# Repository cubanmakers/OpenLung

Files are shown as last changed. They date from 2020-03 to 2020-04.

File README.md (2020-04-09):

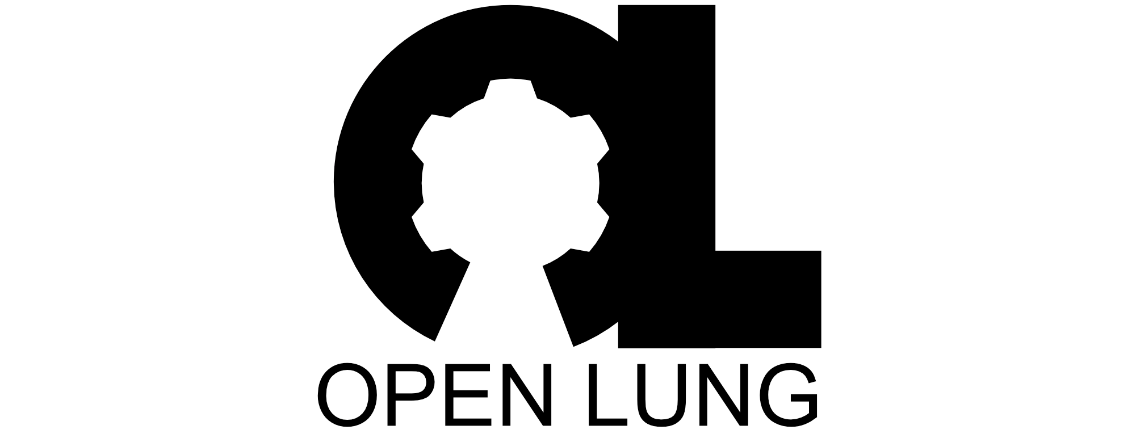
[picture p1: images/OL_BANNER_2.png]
OpenLung


# Disclaimer

*The plans, documents and other materials (“Material”) contained on this website are intended to facilitate the design of a prototype reproducible medical device to be used if required during the Covid-19 pandemic. The Material is not itself a medical device. The Material has not been tested and has not been approved for use in humans or animals by any regulatory authority of any country.*

*By using the Material, you are agreeing to the following disclaimer.*

*OpenLung / Open Source Ventilator offers the Material as-is and as-available, and makes no representations or warranties of any kind whatever concerning the Material, whether express, implied, statutory, or other. This includes, without limitation, warranties of merchantability, fitness for a particular purpose, non-infringement, absence of latent or other defects, accuracy, or the presence or absence of errors, whether or not known or discoverable.*

*To the extent possible, in no event will OpenLung / Open Source Ventilator be liable to you on any legal theory (including, without limitation, negligence) or otherwise for any direct, special, indirect, incidental, consequential, punitive, exemplary, or other losses, costs, expenses, or damages arising out of the Material or use of the Material, even if OpenLung / Open Source Ventilator has been advised of the possibility of such losses, costs, expenses, or damages.*

*Any ventilator system that has not been approved by a competent medical device regulatory authority may not deliver to the user the ability to properly monitor and control tidal volume, inspiratory pressure, inspiratory: expiratory ratio, heart rate, nor provide the user with the ability to monitor and control positive-end expiratory pressure (PEEP), peak inspiratory pressure (PIP) or to adapt to individual patient requirements.  Inability to monitor and/or control any of these factors can cause death or serious permanent injury.*

*The disclaimer of warranties and limitation of liability provided above shall be interpreted in a manner that, to the extent possible, most closely approximates an absolute disclaimer and waiver of all liability.*

# Low Resource Bag Valve Mask (BVM) Ventilator

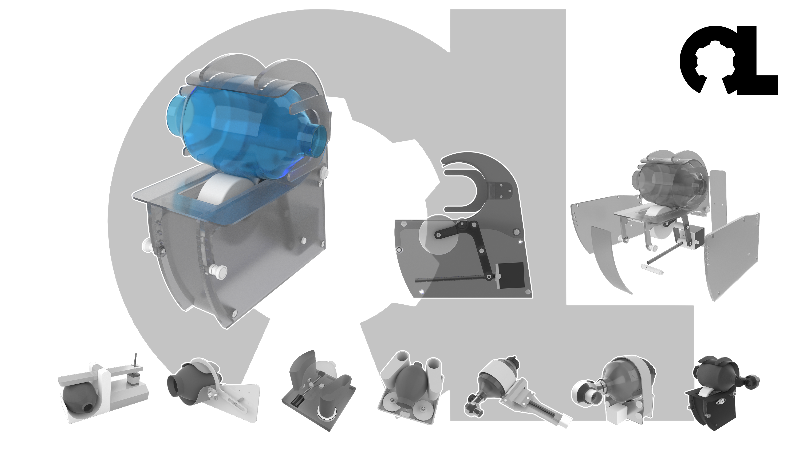
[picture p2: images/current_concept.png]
Current Mechanical Concept


- This project was jumpstarted by the COVID-19 global pandemic as a result of the community discussion on a Facebook group called Open Source COVID19 and OpenSourceVentilator, this is why I created a GitLab project for a new open-source product called **OpenLung**.
- More specifically, this project was created in a discussion surrounding low cost **Bag Valve Mask** (**BVM** or **AmbuBag**)-based emergency respirators wherein prior solutions had been developed.
- The first device discussed came from an [MIT research group](https://web.mit.edu/2.75/projects/DMD_2010_Al_Husseini.pdf) comprising of the following persons: Abdul Mohsen Al Husseini, Heon Ju Lee, Justin Negrete, Stephen Powelson, Amelia Servi, Alexander Slocum and Jussi Saukkonen.
- The second device arose from a [Rice University Mechanical Engineering student group](http://oedk.rice.edu/Sys/PublicProfile/47585242/1063096) comprising of the following persons: Madison Nasteff, Carolina De Santiago, Aravind Sundaramraj, Natalie Dickman, Tim Nonet and Karen Vasquez Ruiz.
- This project seeks to combine and improve the efforts of these two projects into a more simple and reliable device that consists mostly of easy to source or 3D printed parts.
- Benefits: Can be mass-produced, touch points use certified components, small and simple mechanical requirements, previous research and testing in this area, adaptable to both invasive tubing and masks.

# Design Requirements

- Project Requirements are listed [here](requirements/design-requirements.md).

# How To Contribute

-  To contribute to this open-source project please follow the contribution guidelines as outlined [here](CONTRIBUTING.md).

# Project Teams
| Team | Directory | Issue Label |
|---|---|---|
| Requirements | [requirements](/requirements) | ~"Requirements" |
| Mechanical Concepts | [mechanical-concepts](/mechanical-concepts) | ~"Mechanical Concepts" |
| Control Electronics | [control-electronics](/control-electronics) | ~"Control Electronics" ~"Controller Software" |
| Sensor Layout and Specifications | [control-electronics](/control-electronics) | ~"Sensor Hardware" |
| Housing Concepts | [housing-concepts](/housing-concepts) | ~"Housing Concepts" |
| Humidifier Concepts | [humidifier-concepts](/humidifier-concepts) | ~"Humidifier Concepts" |
| BVM Filtration | [bvm-filtration](/bvm-filtration) | ~"BVM Filtration" |
| Regulatory | [regulatory](/regulatory) | ~"Regulatory" |
| Testing | [testing](/testing) | ~"Testing" |

# This document in other languages:
| | | Language | Translations | | |
|---|---|---|---|---|---|
|[english](README.md) | [català](translations/README-ca.md) | [čeština](translations/README-cz.md)| [deutsch](translations/README-de.md) | [español](translations/README-es.md) | [français](translations/README-fr.md) |
| [日本語](translations/README-ja.md) | [nederlands](translations/README-nl.md) | [polski](translations/README-pl.md) | [português](translations/README-pt_BR.md) | [Română](translations/README-ro.md) | [Русский](translations/README-ru.md) |
| [svenska](translations/README-sv.md) | [türkçe](translations/README-tr.md) | [汉语](translations/README-zh-Hans.md) | [漢語](translations/README-zh-Hant.md) |[عربى](translations/README-ar.md)|---|

*Contribute by translating this ReadMe.md file into other languages [here](/translations).*

# Image Licensing



Except where otherwise noted, image content on this repository is licenced under a [Creative Commons Attribution-ShareAlike 4.0 International License](https://creativecommons.org/licenses/by-sa/4.0/).

*Repository managed by [OpenLung](https://openlung.org/) and [OS Ventilator Ireland](https://opensourceventilator.ie/) Communities*

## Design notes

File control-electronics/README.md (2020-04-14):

# Control Electronics for the Open Source Ventilator & Open Lung initiatives
---
## Scope
- **To provide an electronic system to control, sense, and interface the Bag Valve Mask (BVM) ventilator**

- To develop electronic modules to be used as building blocks in the control electronics system design

## Readme Index
- Definitions
- Overview
- Block Diagram
- Control Loop
- How to help
- Directory Structure

## Definitions
- **Electronic System (ES):** is a complete electronic product capable of delivering all the mandatory requirements for the functioning of the BMV. An ES can be integrated in a single Printed Circuit Board (PCB), or can be a motherboard-backplane connecting multiple electronic modules to deliver the final system functionality needs as a multiboard assembly *(i.e. an arduino board with multiple hats would be called "multiboard assembly");*

- **Electronic Module (EM):** is a self contained electronic device that delivers a specific requirement necessary for the functioning of the BMV *(i.e. an Arduino hat, like PoE, Relay driver, etc. would be called "Electronic Module")*

- **Concept specific**: either an EM or ES designed with a very specific mechanical concept in mind, following closely the requirements of that specific concept;

- **Concept agnostic**: either an EM or ES designed by following the ES design guidelines to be used on multiple mechanical concepts. These designs are made around the worst case scenario that's considered by the team;

- **User**: the medical figure responsible for setting and monitoring the ventilation of a patient

## Overview
The Electronics System is responsible for monitoring the respiratory status of a patient and provide ventilation support as defined by the user via a user interface.

The ES is divided into functional blocks (EM)s to ease development and collaboration. The division of a broader system into little sub modules facilitates the work of the designer by providing a very clear requirement and constraints to follow.
By keeping the constraints constant for all the versions a module might have, the integration in a complete ES at later stage is facilitated.

The ES monitors sensors and controls an electrical actuator to provide mechanical movement for the ventilation. As the movement is initiated, the ES closely follows the sensor EM to correct the motor actuation and follow the user predefined inputs.

The ES provides visual and auditory alarms in case certain monitored readings are outside the preferred range selected by the user, or in case of complete power failure during critical operation (ventilation).

The ES provides a redundant power supply line selection, with main and backup line, enabling hot swap operations of the primary line.

The ES provides a clear user interface, showing all the variables set by the user and their readings from the system. The interface should also show the time evolution of critical variables to be monitored.

## Block Diagram


A Guideline of the electronic system block diagram is here shown. Blocks unrelated to the electronics are not included. The pneumatic system and patient blocks are shown only for reference as the system, at least in its high level hardware architecture, is patient and pneumatic system agnostic. Blocks are coloured to highlight different areas of development.The control loop is also highlighted.

## Control Loop
The control loop, also identified as “Feedback Loop”, is the loop that defines the system behaviour during ventilation.

A closed loop control is the best way to ensure the system is operating safely and by respecting all the settings.

An example of closed loop functioning is here detailed:
1. The User (Medical responsible) sets a MODE of operation, pressure and volume data in the input/output interface
2. The Interface communicates all the data to start the ventilation to the MCU.
3. The MCU computes the sequence of movements to be done by the motor to achieve the desired behaviour, based on pre-calibrated reference variables, and outputs a trajectory stored in the MCU.
4. The MCU activates motion of the motor by issuing commands to the Electrical Motor Control.
5. The Motor control commands the stepper motor accordingly.
6. The stepper motor compresses-depresses the pneumatic system providing ventilation to the patient.
7. The pressure sensors connected to the pneumatic circuit provide feedback on the current pressure and volume being transferred in the patient’s lungs.
8. The MCU reads the sensors and computes if the system is following the pre-computed trajectory.
9. The MCU computes the correction (if needed) to keep the system on trajectory and goes to step 4.
10. Interrupt: if new commands are being issued by the Input/Output panel, the MCU immediately computes the new trajectory from the current point and goes to step 4.

## How to help

1.  Give a brief look to the task list below. This will give you an idea of what tasks are waiting someone to develop them, and what are currently being worked on / are considered done and ready for manufacturing.
2.  Identify the taks you would like to work on.
3.  Consult the [System Design Specification Document](https://docs.google.com/document/d/1OEBElTORT_hLxyU2gSYZyEBKLmrnHysd38e4w1xVEWE/edit?usp=sharing) to gain insight on what are the detailed requirements for that task.
4.  If you have any question, doubt or suggestion, contact one of the coordinators.
5.  Start developing, fork this directory, upload your files, and request a merge!

## Tools

#### PCB design CAD:  
- **Altium Designer 20 is strongly preferred**, a free trial period of 30 days can be requested when downloading the software for the first time.
- **KiCAD** is accepted, but the main development work is currently being done under Altium Designer.

#### PCB Simulation tools:
- If you need to simulate anything, **Saturn PCB toolkit** is a nice and easy place where to start.

## Task List

* [ ]  Motherboard design (Altium 20) (design ongoing...)
* [x]  Motor Control Board Design (Altium 20)
* [ ]  Alarm Board (Altium 20) (design ongoing...)
* [x]  Power Regulation, protection and selection Board (Altium 20) (design done)
* [ ]  Sensor Board (Altium 20)
* [ ]  Battery Management System Board (Altium 20)

## Directory structure
- **Concept-specific-ES**: Directory into which ES designs developed for specific mechanical concepts should be placed, naming convention inside this folder must follow the same naming convention of the mechanical concept
    - **Controller-concept-1**
    - ...
    - **Controller-concept-xy**
    - 

- **Concept-agnostic-ES**: Directory into which ES designs developed to provide all the system requirements while being concept agnostic must be placed. A name must be assigned to each concept.
    - **Controller-abc**
    - ...
    - **Controller-def**
    - 

- **Electronic-Modules**: Directory into which EM designs developed to provide a specific functionality must be placed. EM can be both agnostic and specific. When creating the sub directory in the respective category, the type must be highlighted shortly in the name of the directory itself.
    - Alarm
    - Power Regulation
    - Sensors
        - EM-2Flow-2Pressure
        - ...
    - User Interface
        - EM-Graph_480x320_UART
        - ...
        - EM-Graph_800x480_SPI
    - Motor Driver
        - EM-NEMA_17_12V
        - ...
        - EM-NEMA_23_48V
        - EM-Stepper-60V_2Amp
        - 

- **Support-files** Anything to support the electronics control development

## Electronic system coordinator(s)
|GitLab|Slack|
|---|---|
|@nadimconti|@NadimConti|
| | |

## Slack Channels:
- design-hardware
- ele_control-systems

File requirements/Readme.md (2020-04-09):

# CONCEPT:
---
## Scope:
- Requirements necessary to complete this project in compliance with UK Emergency Ventilator Standards

## Overview:

## COVID-19 ARDS Ventilator

- ARDS - acute respiratory distress syndrome
- From https://www.propublica.org/article/a-medical-worker-describes--terrifying-lung-failure-from-covid19-even-in-his-young-patients
- “It’s called acute respiratory distress syndrome, ARDS. That means the lungs are filled with fluid. And it’s notable for the way the X-ray looks: The entire lung is basically whited out from fluid. Patients with ARDS are extremely difficult to oxygenate. It has a really high mortality rate, about 40%. The way to manage it is to put a patient on a ventilator. The additional pressure helps the oxygen go into the bloodstream.”
- “With our coronavirus patients, once they’re on ventilators, most need about the highest settings that we can do. About 90% oxygen, and 16 of PEEP, positive end-expiratory pressure, which keeps the lung inflated. This is nearly as high as I’ve ever seen. The level we’re at means we are running out of options.
- “In my experience, this severity of ARDS is usually more typical of someone who has a near drowning experience — they have a bunch of dirty water in their lungs — or people who inhale caustic gas. Especially for it to have such an acute onset like that. I’ve never seen a microorganism or an infectious process cause such acute damage to the lungs so rapidly. That was what really shocked me.”
- Medtronic (and others) design and build the ‘Ferrari’ of ventilators, OSVentilator Project intends on designing and building a ‘bicycle’

## Scope

- Develop a low-cost, open source ventilator for emergency use to provide ventilation for COVID-19 ARDS patients that have no access to existing ventilators due to overwhelming demand on the medical system of any given country.
- All mechanical elements ‘in the patient airway’ must be medically approved. Control electronics and software must be developed in line with existing medical device standards.- 
- People **_will die_** if this device doesn’t operate correctly

### Indication

The OpenLung device is indicated:
1. As an accessory to a bag valve mask
2. For patients in an acute emergency during complications of COVID-19
3. Patients will most commonly be experiencing acute respiratory distress (ARDs), they may or may not be spontaneously breathing and they are likely ventilator dependent.

### Environments of use

An OpenLung device can be used in three different environments.
1. Acute Hospital Environment
2. Ambulatory scenario within the hospital
3. Transport situation (e.g. ambulance)

## Ventilator Specifications

Three common modes of control in Ventilators:
1. Volume Control
2. Pressure Control
3. Pressure Regulated Volume Control (PRVC)

## Definitiona

- Minute Ventilation (MV) = Tidal Volume (VT) x Respiratory Rate (RR)
- MV = amount of air a patient moves in a minute
- MV can be 5 - 10 lpm in a normal patient but can be 30lpm in a sick patient
- FS02 - Flow source O2. The flow from the supply.
- FDO2 - Flow delivered O2. The flow of O2 at the patient mask.
- FiO2 - Flow (inspired) O2. The O2 in the patient.

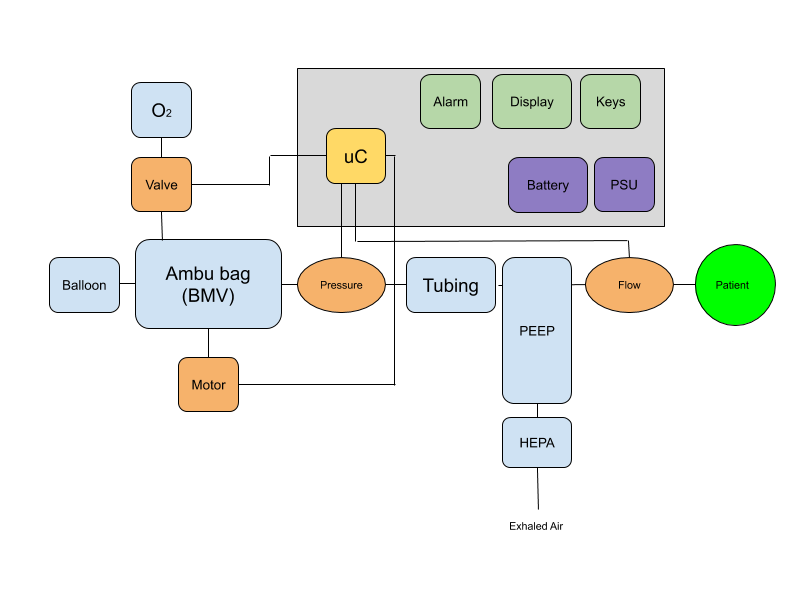
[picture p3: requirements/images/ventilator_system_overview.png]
System overview image_tooltip

    Fig. 1: System overview

## These appear to be the accepted ranges for treating Convid-19 ARDS - from UCC’s ARDS Ventilatory Management PDF:

<table>
  <tr>
   <td><strong>Variable</strong>
   </td>
   <td><strong>Range</strong>
   </td>
   <td><strong>Accuracy</strong>
   </td>
   <td><strong>Settings</strong>
   </td>
   <td><strong>Default</strong>
   </td>
   <td><strong>Notes</strong>
   </td>
  </tr>
  <tr>
   <td><strong>Tidal Volume (V<sub>T</sub>)</strong>
   </td>
   <td>4-6ml/Kg IBW*
<p>
(205 - 530ml)
   </td>
   <td>±???
   </td>
   <td>±1ml/Kg
<p>
(35ml)
   </td>
   <td>-
   </td>
   <td>
   </td>
  </tr>
  <tr>
   <td><strong>Respiratory rate (R<sub>R</sub>)</strong>
   </td>
   <td>15-35bpm
   </td>
   <td>???
   </td>
   <td>±2bpm
   </td>
   <td>15bpm
   </td>
   <td>
   </td>
  </tr>
  <tr>
   <td><strong>I:E Ratio</strong>
   </td>
   <td>1:1 - 1:5
   </td>
   <td>???
   </td>
   <td>???
   </td>
   <td>
   </td>
   <td>
   </td>
  </tr>
  <tr>
   <td><strong>Plateau Airway Pressure (P<sub>AW</sub>)</strong>
   </td>
   <td>10-30cmH<sub>2</sub>O
   </td>
   <td>???
   </td>
   <td>???
   </td>
   <td>&lt; 30cmH<sub>2</sub>O
   </td>
   <td>If > 35 V<sub>T</sub> needs to be decreased to 5 or 4ml/Kg IBW
   </td>
  </tr>
  <tr>
   <td><strong>Driving Pressure</strong>
<p>
<strong>(P<sub>AW</sub>-PEEP)</strong>
   </td>
   <td>???-15cmH<sub>2</sub>O
   </td>
   <td>???
   </td>
   <td>???
   </td>
   <td>
   </td>
   <td>
   </td>
  </tr>
  <tr>
   <td><strong>PEEP</strong>
   </td>
   <td>5-16cmH<sub>2</sub>O
   </td>
   <td>???
   </td>
   <td>±1
   </td>
   <td>???
   </td>
   <td>Does this need to be controlled and set remotely or can it be done manually?
   </td>
  </tr>
</table>

## (*)Calculate Ideal Body Weight (IBW, Kg) using patient height (cm):

<table>
  <tr>
   <td><strong>Male</strong>
   </td>
   <td><strong>Female</strong>
   </td>
  </tr>
  <tr>
   <td>= 50+0.91x(height in cm-152.4)
   </td>
   <td>= 45.5+0.91x(height in cm-152.4)
   </td>
  </tr>
</table>

### Humidification

- Out of scope. This could be considered a ‘comfort feature’ for long-term use.

### Nebulizer

- Nebulizers are used to deliver inhaled prostacyclin analogues in patients with severe ARDS and refractory hypoxemia. See ISO/AWI 27427 for connector specs.

### Mask or Tubing

- Depends on patient’s clinical condition.
- Non-invasive mask or helmet ventilation is typically used if the patient is alert, reasonably stable and the main problem is severe hypoxemia and the lungs are not too stiff.
- Endotracheal intubation is generally required if the patient is too agitated to wear mask, is exhausted, has decreased level of consciousness or is profoundly hypoxemic (low level of oxygen in arterial blood).
*From [http://rc.rcjournal.com/content/56/1/52](http://rc.rcjournal.com/content/56/1/52)*

### Cycling of the Mechanical Ventilator Breath

- The change from inspiration to expiration is a crucial point in the mechanically ventilated breath, and is termed "cycling".

#### Cycling Mechanisms:
*   Pressure (PMAX - I’m using this for want of a better term ~ there may be a standard term used here)
    *   When a set pressure is reached, inspiration is cycled into exhalation. Most commonly used during alarm - if a patient becomes extremely asynchronous (in their breathing) or coughs, a high-pressure alarm may be triggered and the inspiration phase will end.
*   Time (TCY)
    *   Switch from inspiration to exhalation when a set time period is reached. This can be achieved by setting the **_Resp Rate, Inspiratory Time or I:E Ratio_**. _Many ventilators terminate the inspiratory phase after 3-5secs._
*   Volume (VT & VTMAX)
    *   Inspiration stops once VT is reached. Cycling to exhalation phase will occur when VT OR VTMAX is reached.
*   Flow (FCY)
    *   During pressure-support ventilation (PSV), the patient both triggers and cycles the breath. (See diagram below) When a patient's inspiratory flow decreases to 25% of  peak inspiratory flow, the breath would cycle to the exhalation phase.

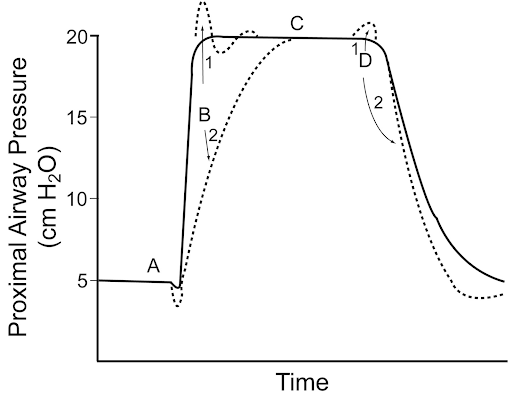
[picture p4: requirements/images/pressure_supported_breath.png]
Pressure supported breath image_tooltip

    Fig. 2: Characteristics of a pressure-supported breath. In this example, the baseline pressure (ie, PEEP) is set at 5 cm H2O, and the pressure support is set at 15 cm H2O. The inspiratory pressure is triggered at point A by a patient effort, resulting in an airway pressure decrease. The rise to pressure (line B) is provided by the initial flow into the airway. If the initial flow is excessive, the initial pressure exceeds the set level (B1). If the initial flow is low, there is a slow rise to pressure (B2). The plateau of pressure support (line C) is maintained by control of flow. A smooth plateau indicates appropriate flow responsiveness to patient demand. Termination of pressure support occurs at point D and should coincide with the end of neural inspiration. If breath termination is delayed, the patient may actively exhale (the pressure rises above the plateau) (D1). If breath termination is premature, the patient may have continued inspiratory efforts (D2). (Adapted from Reference 18, with permission.)

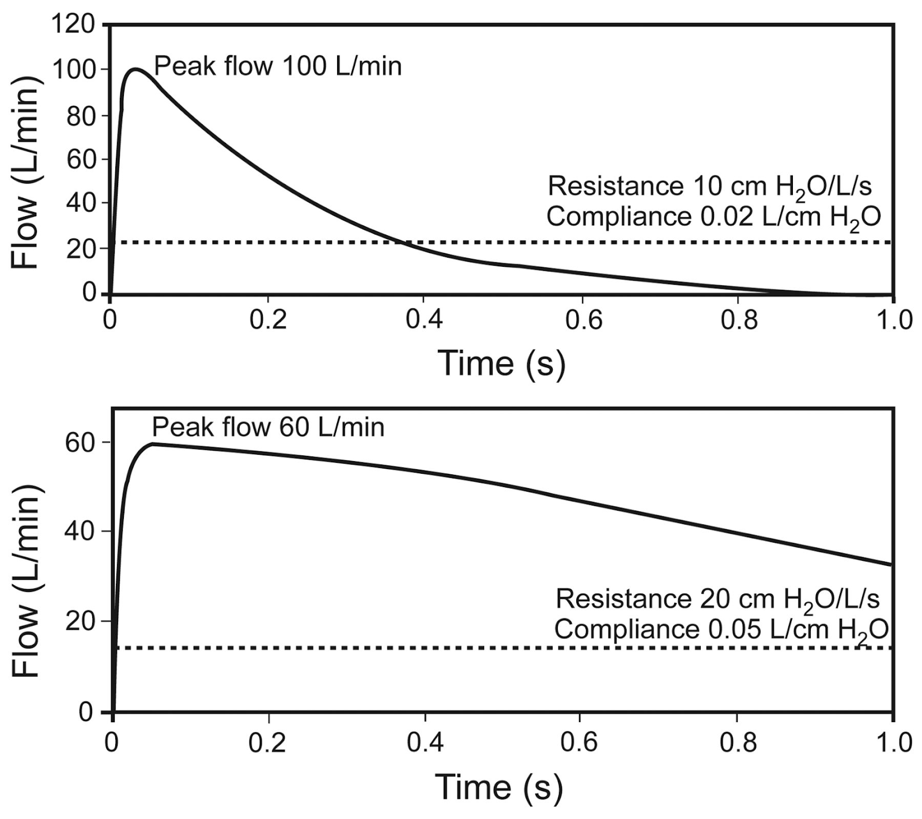
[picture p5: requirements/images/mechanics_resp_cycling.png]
Respiratory mechanics image_tooltip

    Fig. 3: Effect of respiratory mechanics on cycling of pressure support from inhalation to exhalation. Flow cycling is set at 25% of the peak flow, as illustrated by the broken line. The upper panel represents the respiratory mechanics of a patient with restrictive lung disease. The lower panel represents the respiratory mechanics of a patient with obstructive lung disease. In each case the neural inspiratory time is 1.0 second. The breath terminates prematurely in the patient with restrictive lung disease, but the breath is prolonged in the patient with obstructive lung disease. Also note that the peak flow is greater in restrictive lung disease, and the pressure decrease is more rapid in restrictive lung disease. (Adapted from Reference 19.)

### Alarms
1. There must be a visual display of an alarm situation. This must be visible from XXm.
2. There must be an audio alarm, with continuous sound of YYdB.
3. Alarms may be silenced, for a period of ZZ seconds, via the user interface.
4. If the underlying alarm condition has not been cleared, the alarm will sound again.

#### There are 3 types of alarms:

1. Input - power supply and air / oxygen source
2. Control - incorrect settings of control variables
3. Output - incorrect outputs from the Ventilator to the patient

<table>
  <tr>
   <td>
<strong>Alarm type</strong>
   </td>
   <td><strong>Min</strong>
   </td>
   <td><strong>Max</strong>
   </td>
  </tr>
  <tr>
   <td><strong>Minute Ventilation (MV)</strong>
   </td>
   <td>&lt;5lpm
   </td>
   <td>>30lpm
   </td>
  </tr>
  <tr>
   <td><strong>Peek Pressure</strong>
   </td>
   <td>
   </td>
   <td>>??
   </td>
  </tr>
  <tr>
   <td><strong>Tidal Volume (VT)</strong>
   </td>
   <td>&lt;200ml
   </td>
   <td>>600ml ???
   </td>
  </tr>
  <tr>
   <td><strong>Flow</strong>
   </td>
   <td>??
   </td>
   <td>??
   </td>
  </tr>
  <tr>
   <td><strong>Inspired Gas Temp</strong>
   </td>
   <td>??℃
   </td>
   <td>??℃
   </td>
  </tr>
  <tr>
   <td><strong>O2 Concentration</strong>
   </td>
   <td>??%
   </td>
   <td>??%
   </td>
  </tr>
  <tr>
   <td><strong>Input Power</strong>
   </td>
   <td>
   </td>
   <td>
   </td>
  </tr>
  <tr>
   <td><strong>Battery SOC</strong>
   </td>
   <td>&lt;50%??
   </td>
   <td>Reset alarm >90%SOC
   </td>
  </tr>
  <tr>
   <td><strong>Failed Self Test</strong>
   </td>
   <td>
   </td>
   <td>
   </td>
  </tr>
  <tr>
   <td>
   </td>
   <td>
   </td>
   <td>
   </td>
  </tr>
</table>

- Are there Alarm standards?

### Sensors & Control Valves

- PEEP - Adjustable between 5-16cmH<sub>2</sub>O. Need to source a PEEP valve.
- SpO2 - can we get this from an external, existing hospital sensor?
- FSO2 / FDO2 / FiO2??? - O2 sensors? Need medical ones?
- O2 flow - valve???
- Flow - Sensirion SFM3300 or similar (I2C interface)
- Pressure - ??? Can we measure this outside of the ‘patient airway’?
- Accuracy???

### Power Supply

- Mains power.
- Medical grade PSU ideally operating on universal input - 90V - 240V AC, 50 - 60Hz, with an output of XX V DC, @ YY Amps.
- Battery backup. ?? V, ?? Ah battery providing power to the entire system for 60 mins. Battery should recharge once mains power is returned. Battery should recharge to 100% SOC within YY mins.

### User Interface
- What must be displayed?
- What is the minimum?
- What’s nice to have?
- Method of interacting with display. Buttons or rotary encoder.

### Self Tests
- Battery. Test battery is operational and can power the entire device.
- Sensors. Perform built-in self test on all sensors.
- Motors. Ensure motors are operational and moving within set limits.
- Microcontroller. Tests?

### Safety
- Fire? Wiring?
- Fail-safe - motors? Valves fail open/closed?
- HEPA filters

### Mechanical
- Widely available materials
- Easy clean surfaces that are not affected by hospital cleaning products??

### Cost
- Bill of Materials &lt; $YYY or €XXX

### Ventilator Standards

*Standards relating to ventilator use, operations and design*

- ASTM F 1100-90 (Standard Specifications for Ventilators Intended for Use in Critical Care) (Withdrawn without replacement in 2004)
- ASTM F 1246-91 (Standard Specification for Electrically Powered Home Care Ventilators, Part 1-Positive-Pressure Ventilators and Ventilator Circuits) ([LINK](https://civilengineersstandard.com/wp-content/uploads/2019/02/F-1246.pdf))
- IEC 6061-2-12(Standard for Critical Care Ventilators)
- ISO 80601-2-12:2020 Medical electrical equipment — Part 2-12: Particular requirements for basic safety and essential performance of critical care ventilators
- ICS 11.040.10 (ANAESTHETIC, RESPIRATORY AND REANIMATION EQUIPMENT INCLUDING MEDICAL GAS INSTALLATIONS)
- ISO 10651-3:1997 (Lung ventilators for medical use — Part 3: Particular requirements for emergency and transport ventilators)
- ISO 10651-4:2002 (Lung ventilators — Part 4: Particular requirements for operator-powered resuscitators)
- ISO 10651-5:2006 (Lung ventilators for medical use — Particular requirements for basic safety and essential performance — Part 5: Gas-powered emergency resuscitators)
- ISO 19223:2019 (Lung ventilators and related equipment — Vocabulary and semantics)
- ISO/TR 21954:2018 (Guidance on the selection of the appropriate means of ventilation based on the intended patient, use environment, and operator)
- ISO 80601-2-72:2015
- Medical electrical equipment — Part 2-72: Particular requirements for basic safety and essential performance of home healthcare environment ventilators for ventilator-dependent patients
- ISO 80601-2-79:2018
- Medical electrical equipment — Part 2-79: Particular requirements for basic safety and essential performance of ventilatory support equipment for ventilatory impairment
- ISO 80601-2-80:2018
- Medical electrical equipment — Part 2-80: Particular requirements for basic safety and essential performance of ventilatory support equipment for ventilatory insufficiency
- ISO/DIS 80601-2-87 (Medical electrical equipment — Part 2-87: Particular requirements for basic safety and essential performance of high-frequency ventilators)
- ISO/FDIS 80601-2-84 (Medical electrical equipment — Part 2-84: Particular requirements for basic safety and essential performance of ventilators for the emergency medical services environment)
- BSEN 794-3:1998 +A2:2009 Particular requirements for emergency and transport ventilators

### Connectors for Respiratory Devices

- ISO/AWI 27427 Nebulizing systems and components (Under Development)
- ISO/AWI TR 22175 Connectors for respiratory devices (Under Development)

### References

- [University College Cork Covid-19 Resource Centre](https://ucc.instructure.com/courses/22984)
- [UCC Covid-19 Critical Care](https://ucc.instructure.com/courses/22984/pages/critical-care)
- [UCC Covid-19 induced ARDS - protective lung ventilation (Meeke 2020)](https://ucc.instructure.com/courses/22984/files/1700272/download?wrap=1)
- [The Center for Safety, Simulation and Advanced Learning Technologies](https://simulation.health.ufl.edu/technology-development/open-source-ventilator-project/)
- [CSSALTlab Open Source Ventilator - Github repo](https://github.com/CSSALTlab/Open_Source_Ventilator)
- [Pressure Regulated Volume Control (PRVC): Set it and forget it?](https://www.sciencedirect.com/science/article/pii/S2213007118303757)
- [Cycling of the Mechanical Ventilator Breath](http://rc.rcjournal.com/content/56/1/52)
- [https://youtu.be/-ksxZeKpbjw](https://youtu.be/-ksxZeKpbjw)
- <span style="text-decoration:underline;"><span style="text-decoration:underline;">https://my.clevelandclinic.org/-/scassets/files/org/respiratory/fundamentals-of-mechanical-ventilation.ashx?la=en&fbclid=IwAR0CA5Bnv8oVnQriB47-NYzJuLUHX2M3m2jY4KvQ-zFPjmExGzFwvSLvnHg</span>

## Team Lead(s):
|Name|GitLab|Slack|
|---|---|---|
| Mark Layden | @mleyden | Mark Layden |
| Trevor Smale | @trevorsmale | Trevor Smale |
| Cameryn Rhosyn | @camrhosyn | Cam |
| Andrew Finkle | @finks | Andrew Finkle |

## Additional Documents
- [Google Doc](https://docs.google.com/document/d/1h77FkKXqPOwVqfOj-PIJSjYX9QiEx69Av2gYuzqZolw/edit?usp=sharing)
- [Early Notes from Trevor Smale (@trevorsmale)](/requirements/resources/design-requirements.md)
- [Important Design Parameters](/requirements/resources/IMPORTANT_DESIGN_PARAMETERS.md)

## Slack Channels:
-

## Issue Labels:
- Legal Requirements
- Technical Requirements

## References:
- [National Regulatory Guidances on Ventilators](regulatory)

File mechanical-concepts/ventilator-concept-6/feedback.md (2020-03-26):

# Concept 6
## NC Sandwich Pulley Concept

### Notes:
- Removes custom 3D parts
- Design philosophy evolved towards more flat metal construction.
- This could be mass produced through stamping, but also could be CNC or 3D Printed for prototyping/testing (and in areas with less access to resources, less regulation).
- Stamping will bring part manufacturing down to seconds and easier to certify materials/methods, and there are localized metal shops in many cities.
- First concept widely tested by OpenLung/OSV community, branches started to form with improvements.

### Issues:
- Simple, but lacks some capabilities (perhaps?)
- Belt may cause friction issues on the BVM after continued work.
- Not Hot-swappable (could add buckle or another connector)

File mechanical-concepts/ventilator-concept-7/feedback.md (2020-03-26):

# Concept 7
## Radial Arm Depressor

## Notes:
- Improvements on concept 6 based on community feedback.
- Combines the pulley idea with a depressor and a flat basket to cradle the BVM.
- This removes friction/stress to the BVM
- Roller can be manually adjusted to change volume/pressure.
- Sticky medical tape (can’t remember the name) can be applied to the roller to assist retraction (filling BVM up)

## Issues:
-

---
### Pressure Cylinder v2 won't fit the rings around them (tolerance problem)
### Submitted by: @erikdebruijn
I tried to mate the parts "Pressure Cylinder v2" (white) and "Pressure_Cilinder_ring_1-OD70mm_v2" (shown in red) but they simply won't fit. Maybe by heating it up and using force I can get it in, but that is too much labor and we don't want to introduce process variation. It's much better to reduce the outer diameter of the "Pressure Cylinder v2" since:

We don't want to change all the different outer parts (red).
Since I don't have native design files I cannot make a change to the CAD file (issue #96). I'll reprint the object with an offset of -0.4 mm.

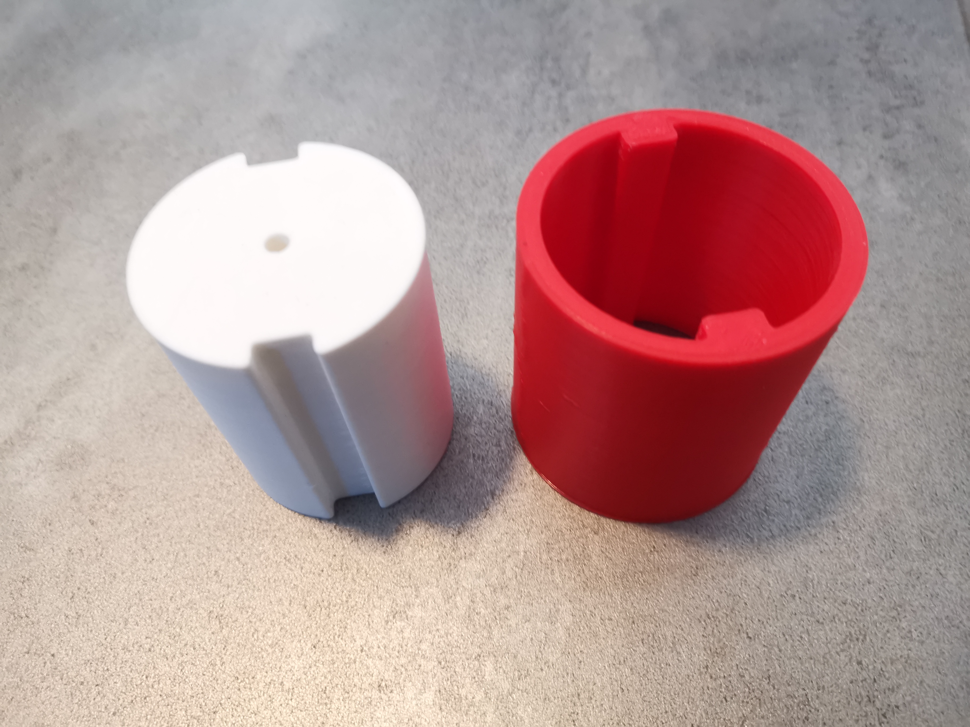
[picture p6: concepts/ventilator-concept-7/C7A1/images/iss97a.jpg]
issue97a


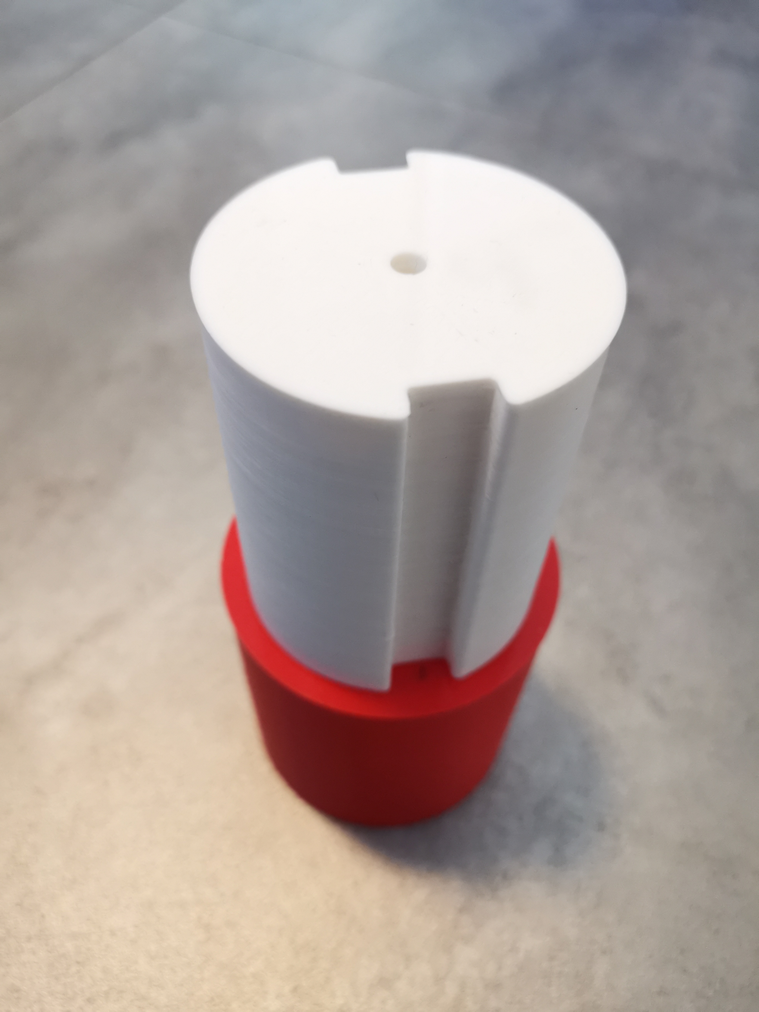
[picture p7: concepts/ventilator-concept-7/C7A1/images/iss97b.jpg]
issue97b


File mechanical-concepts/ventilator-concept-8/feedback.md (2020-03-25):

# Concept 8 - Current Concept

## Notes:
### Mechanical:
- Needed to add feature (Tilting) for varying depressions on the fly without touching the electronic interface
- Simplified the depression mechanism to an eccentric cam as testing has shown difficulties with tensions and motor torque on 6
- Seven was overly complicated according to the Hive-mind and close advisors.
- Moreover, belt wear is a big concern. I had under estimated the wear factor on belts which causes fraying and consequently more open surfaces for particles to attach.
- Continuing in regards to the belt, the nylon weave is furthermore not suitable for viral control as it has extensive surface networks and cannot be sterilized easily.
- Moreover, the belt has un-predictable bunching characteristics that would take extensive testing and iteration to control in an engineered manner.
- The overall footprint was too small and required modules to expand into a operational size
- The rollers require inset faces for bearings to properly engage, this was an unexpected twist, essentially making rollers time and process intensive vs flat planes
- Parallelism was also a major reason for altering the mechanism as Kush Babar stated, Pitting happens quickly as a result of eccentric parallelism cause by repetitive vibration and expansion contraction.

### EE

- The electrical engineering is still loosely defined, However most development has been aimed at open source SBC's like RPI and ARD with the thinking that we would have abundant quantities available.
- According to our updated numbers, it looks as though those available supplies are not only being used, but also being considered for a number of new projects as it is familiar to hobbyists.
- Andrew and I have been reaching out to many people personally in regards to the development of the electronics design, production and availability without getting any solid information.
- There is a man involved from Texas named Sam Pedroggy who was offering up a large supply of custom displays, when considered in contrast to the development community we were unsure about the efficacy of branching such dev commitments.
- We are currently in talks with larger MFG (Digikey) to assess the possibility of a custom open sourced driver board, so that we don't have to mishmash components.

### Function

- It was important to address the motion path of the mechanism as it also effects the usability and safety of the machine.
- We need to reduce friction to near zero for long cycle times.
- Any wear needs to be addressable by way of field servicing

### Manufacturability

- Due to constantly increasing volume requirements we have had to assess and re-assess the potential process. This device takes into consideration, the possibility of producing
- 1000 per day, or 100 per assembler.
- We will need to utilize the stamping infrastructure of automotive plants to actually supply the demand.
- Laser cutting is a stop gap measure to get testing and have alternate design available early.

### Aesthetic

- Needs to look inviting or not intimidating to newly initiated users
- Needs to imply operational characteristics
- Needs to take a bump or fall
- Needs to be powder-coated for decontamination

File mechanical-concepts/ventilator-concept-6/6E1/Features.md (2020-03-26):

- Quickly adjustable pump volume
- All sheet metal fabrication.
- Only two trivial bends. No large radii. No internal folds.
- Quasi rotary encoder with micro switches
- compatible with a strong 12V gear motor
- Low friction on the belt and ambubag

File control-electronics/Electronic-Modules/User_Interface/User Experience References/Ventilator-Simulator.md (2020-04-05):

# HAMILTON C6 VENTILATOR SIMULATOR (FREE)

The simulation software features:  

1. A fully simulated ventilator graphical user interface (GUI) with all control and alarm settings and most ventilation modes 
2. Real-time monitoring values, curves, and visualization for all relevant parameters
3. A physiological patient model including various adjustable patient conditions: normal, COPD, and ARDS
4. Monitoring parameters for the patient’s oxygenation and ventilation, including a simulated BGA

## Files and downloads

- USER INSTRUCTIONS: https://www.hamilton-medical.com/it/dam/jcr:6a72fa07-aaa6-4daa-9471-c511041cabc1/HAMILTON-C6%20simulation%20IFU.pdf
- Windows Installer: https://www.hamilton-medical.com/it/dam/jcr:7799e4cd-4a06-43cf-9b6d-475f5b521b3f/HAMILTON-C6-SETUP.exe
- MACOS: https://www.hamilton-medical.com/it/dam/jcr:4e2a0bf6-6a37-4b43-ac9e-6451c398c41a/HAMILTON-C6.zip
- iOS: https://itunes.apple.com/us/app/hamilton-c6-simulation/id1440816818
- Android: https://play.google.com/store/apps/details?id=com.HamiltonMedical.c6simulation

- Original page: https://www.hamilton-medical.com/it/Products/Mechanical-ventilators/HAMILTON-C6.html

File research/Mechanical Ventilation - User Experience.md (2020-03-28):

DOCUMENT WITH PICTURES:

https://docs.google.com/document/d/1eTu0q5RjkaKut7kVIUAN8q9fsSBreSZQOf7-ojzA6GY/edit?usp=sharing

Transcription:

Mechanical VentilatioIn overview – UX focus
Main source: 
https://www.medcram.com/courses/COVID19-ventilator-mechanical-ventilation

AIM: to maintain homeostasis between exhaled CO2 and inhaled O2 concentrations

Patient connected to ventilator via endotracheal tube (ET), provides airway protection, avoiding liquids and fluids from going down, or also providing full support for the respiratory act.
The ET tube is built to pass the vocal cords roughly ½ the length of the tube, going towards the lungs branch, there, with an airway protection balloon, we can provide airway protection. On top of the balloon ( mouth side ), a tube can be present to provide subglottic suctioning, meaning removal of liquids or solids that accumulated on top of the airway protection. 

To start ventilating, we can touch multiple parameters: 
Pressure (we can push a certain pressure into the lungs)
Volume (we can transfer a certain amount of air in the lungs)
Rate (we can select the frequency of the respiratory act)
Flow (we can select the speed at which the volume is transferred in and out);
Residual pressure (how much pressure do we always want to be in the lungs, even while pausing between respiratory acts)
Oxygen (how much oxygen we want to supply to the patient)
Control (if the ventilator or the patient is in charge to start the respiratory act)

All of this  is summarized in selecting the operation mode for the ventilator to be operating in

VENTILATOR MODES

AC - ASSIST CONTROL (Continuous Mandatory Ventilation (CMV))

The patient starts the ventilation act (respiratory cycle) by provoking negative pressure build up in the ET (trying to breathe). The negative pressure will then be detected by the ventilator that will start the respiratory act. 

In this case, once the ventilation is triggered, the ventilator will provide the Volume to be set by the user when in AC mode.

Volume can be anywhere between 500-600ml, ideally 8ml/kg og Ideal Body Weight.

NOTE: Respiratory Rate is also an important setting here, i.e. 10 (acts per minute), setting the lower threshold of respiratory acts in one minute. This means that, if the machine does not sense a new trigger (after a previous one) in 60/RR seconds, the machine will automatically start the respiratory act, delivering the set volume.

A patient therefore can never breathe less than the set RR.

NOTE: Compliance is defined as C’ = dV/dP  (first derivative of volume change over pressure change, from (for ideal gas) PV= nRT)

If C’ is high, the lung is said to be very compliant.

There’s a need in AC mode to read the PRESSURE to know the C’ of the lungs.
C’ is not constant, it can change, therefore an ALARM is needed in case the pressure drops or rises to much! USER must be able to set those limits.

PC – Pressure Control

Same as AC mode, but Pressure is set instead of volume, and volume is read by the machine. 
C’ is not constant, it can change, therefore an ALARM is needed in case the Volume drops or rises to much! USER must be able to set those limits.

CPAP (if noninvasive ventilation, mask ) – PEEP (invasive) (Positive expiratory end pressure)
The user sets a constant pressure that the patient is getting (5-20ml of water). This is the pressure that will always be in the lungs to keep the alveoli open.
This mode should have its own dial.

Pressure Support 
Similar to PC, but here the patient triggers every breath

VENT ORDERS
How does a doctor issue an order of ventilation?
i.e. MODE AC, 16, TV 550, FiO2 50, PEEP 5
to be read as: Assist control, 16 RR, Tidal Volume 550ml, 50% Oxygen, end pressure 5ml H20
Note: RR and TV controls the CO2 concentration
Note: FiO2 and PEEP controls the O2 concentration (oxygenation)
Note: the higher the PEEP, the more alveoli you can open, the better the oxygenation.
Chart Example, note that when the ventilator is triggering the breath, no negative pressure peak is detected (which is caused by the patient when trying the breathe) 

PEAK and PLATEAU pressure
When air is going into the lung (dynamic), the resistance is offered by the airways. Once the lungs are inflated, the pressure offered by the lungs is their compliance, not the airways anymore.
Peak pressure has to do with airways
Plateau pressure has to do with the lung compliance
NOTE: if the patient has an issue with the airways, the peak pressure is going to change!
Chart showing the pressures under consideration. The “zero” in the Paw axis is actually the PEEP pressure, which will be >0.

NOTE: if the difference between peak and plateau is above 5mmHg, it is regarded as ELEVATED PEAK PRESSURE, if the pressure alarm is going off, THE USER WILL WANT TO KNOW IF THE PARAMETER THAT IS HIGH IS THE PEAK OR THE PLATEAU PRESSURE
A high peak pressure might mean bronchospasm, secretion, mucus, tip of secretion tube occluded
A  High plateau might mean dorp in C’, PTX, Pulmonary edema, ARDS, Pneumonia

Medical Note for AC mode: increasing the RATE, increases ventilation, but also increases dead space (air that goes into the mouth/trachea, that is not going to be used for the respiration, roughly 150ccm). Usually tough, increasing tidal volume is a more efficient way to increase ventilation as every increase in TV goes directly into the lungs, not like in RR.
Medical Note for AC mode: a too high TV might cause repetitive collapse of the alveoli, inducing inflammation (provoking ARDS, with ARDS therefore, the tidal volume is usually low)!
Note: VERY IMPORTANT, A SUCCESIVE BREATH MUST START ONLY AND ONLY IF THE PREVIOUS IS FINISHED AND AIR LEFT THE LUNGS AS EXPECTED, otherwise the patient might suffer breath stacking and COPD.
Medical note: PEEP opens up the alveoli, but also increase the intra-thoracic pressure, which applies pressure on the heart, and increase pressure in the right atrium. Which translates into lower venous return, and lower cardiac output, which means lower BLOD PRESSURE, therefore, INCREASING PEEP, might lower blood pressure. Anyway, in patients with congestive heart failure, increasing PEEP might save them.

Ventilation CHANGES with ARDS and COPD
Medical consideration (operation flow)
Scenario : settings AC 12, TV 400, FiO2 40%, P5
Blood gas results: 7.26 | 60 | 55 |26
To be read as: 7.26 pH, 60 pCO2, 55 pO2, 26 HCO3-

pH is low, and pCO2 is high, as they go in different directions, it is a respiratory disorder, as pH is low, it is a respiratory acidosis, most likely we are under ventilating, and as pO2 is low as well, we’re under oxygenating. 

To know if the patient is sedated or not is important as the setting AC 12, means the RR is 12, but if they are not sedated, this might mean that they could be breathing faster than a 12 RR. It is important as, if they are not sedated, WE NEED TO KNOW THE ACTUAL RR!  As if we push the RR higher to improve the ventilation, this might not result in a better ventilation (the patient might be already breathing above our threshold!

We therefore need to know both the doct. Settings and the patient response!

Now, to improve the ventilation, we could improve AC12 to AC14-16, and TV is quite low too, so it could be raised to TV 500 (from TV 400), both these changes will improve the pH (increase it) and lower the pCO2. Now, to improve the Oxygenation, we can increase PEEP or FiO2, but If the patient’s blood pressure is on the lower margin, we do not want to increase PEEP, as it will usually increase inter thoracic pressure on the heart and lower the blood pressure as explained before. Therefore, we would increase FiO2. But if the patient doesn’t have marginal blood pressure, and has congestive heart failure (CHF) then we have plenty of venous return, and then they probably could have pulmonary edema in the alveoli, therefore increasing PEEP to i.e. 10, could be a better choice, solving the edema by pushing out the fluid and allowing the heart to work better.

This choice therefore depends on the clinical situation.

Acute Respiratory Distress syndrome  (ARDS)

Inflammatory condition of the lungs -> the lungs become very stiff - > C’  DROPS !

Therefore, we will have elevated plateau pressure. The alveoli will fill with fluid and collapse. TV should be, by research, be limited. Therefore, an open lung approach could be used. The lower the pO2, the higher PEEP is maintained (12, 14). Then, low tidal volume (6-8 ml/kg IBW, measured by height, in the 4-500 range) Alveoli stay open.

COPD patients
very different than ARDS, C’ in this case is very high, the problem here is that the airways at the end of the branch are obstructed, therefore is really hard to get air out of the lungs, which means air gets trapped. Because of this, we have very long expiratory phases. Typically, the patient has high CO2.
Here one might be tempted to increase the RR or TV to lower pCO2, but by doing this we increase the air in the lung, risking respiratory stacks 
Normally, in time terms, the breathing is 1/3 INSPIRATION and 2/3 EXPIRATION. What we can do in COPD is to lower the time it takes to do the inspiration, therefore increasing the IFR (intake Flow Rate), that in normal conditions are around 60 Liters /minute, here they will be around 80 -100 Liters per minute. This way, we can get air in quickly, and have more time for the air to come out.
NOTE:  in this and every situation, FLOW MUST COME BACK TO ZERO AT THE END OF THE RESPIRATORY ACT ! (Risk of hyper inflating).

Liberation from the Ventilator
Protocols in ICU to do (every single day):
Lifting Sedation
Liberation trial - >  move the mode to act as closely as possible to physiological, observe the patient for a few  (2-3) hours and take a blood gas analysis (ABG). If the ABG is good, then it’s a good sign. 
Another index to keep an eye open on is the RSBI (Rapid Shallow Breathing Index, or Tobin Index, RSBT = RR / TV. 
RSBI  index > 105 is a bad sign, you do not want a  patient to come of a ventilator breathing fast and short. 
NIF Index  ( around -30, it’s good) 
MV (Minute Ventilation ) below 15 Liters /Minute, shows that the patient doesn’t need to breathe very fast.

CHECKLIST TO REMOVE PATIENT 
Mechanics of ventilation are Good (completed a liberation trial or more) 	
Mental Status (is the patient mentally alert enough to protect the airway, it can be the first reason why they came in in the first place) 
Secretions (are there copious secretions coming out of the endotracheal tube?);
Air Leak (when deflating the balloon at the end of ET, air should leak!) (there can be Tracheal swellings around the balloon area, stopping air to get out);

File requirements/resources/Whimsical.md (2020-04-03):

## See live Whimsical flow chart [here](https://whimsical.com/4mai9JtqTHAGu6i6qz8Hyy)

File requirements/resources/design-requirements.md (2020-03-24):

# Design Requirements

## Drafted by Trevor Smale (adapted from MIT)

### Previous Designs Inspiring This Project

[Rice University Mechanical Engineering Model](http://oedk.rice.edu/Sys/PublicProfile/47585242/1063096)

Features:
- Easy to use 3 button adjustment scheme (Tidal volume + -)
- High low pressure alerting
- Mostly NC fabrication methods
- Compact and light.

Issues:  
- Multi Material (Complex construction)
- Seemingly fragile components
- Unventilated/cooled electronics
- Low humidity tolerance
- No proper open source files.

[MIT Research Group Design](https://web.mit.edu/2.75/projects/DMD_2010_Al_Husseini.pdf)

Features:
- Ultra reliable cam actuation mechanism
- Simple/repeatable motor diver circuit
- Similar Easy to use 3 button schema
- Hermetically sealed

Issues:
- Multi Material (Complex construction)
- Overtly robust/substantial
- Some specialty parts

### Medical Considerations

- User-specified breath/min (Via button or knob interface)
- Insp./Exp. ratio, tidal volume
- Support modes:
    - PCV (Pressure-controlled Ventilator)
    - VCV (Volume Control Ventilator)
    - Also: Assist Control (Note: assist control is the action of detecting patient effort to breath and it works in different ways according to ventilator mode)
- Positive end-expiratory pressure (PEEP)
- Maximum pressure limiting
- Humidity exchange (built into the mask)
- Infection control (By way of covering the unit in an easily cleaned enclosure)
- Limited dead-space

### Electronics and UI/UX
- Spec an interface (LCD and Buttons)
- Spec feedback sensors for PEEP, low voltage, high and low pressure events.
- Outline interface visually

### Mechanical

- Portable / Stationary (Perhaps the stationary design will be a separate branch)
(Greg: I would index on stationary. The Rice/MIT designs are for dev world. This project assumes use in a resource limited hospital)
- Standalone operation with 1:4 RN:Pt ratio (Full autonomy within hospital setting by way of sensor feedback and adjustment loops)
- Robust mechanical, electrical and software systems (Simple, Corrosion resistant, Vibration resistant, Best crystal oscillator)
- Readily sourced and repairable parts (3D printing)
- Minimal power req (Efficient motor controller)

### Economic

- Low cost ($100.00 US build cost)
- Must fit within standard printer bed in short term.
- Possible Long Term Target: Stamping due to high volume capacity over 3D printing
- Must use *mostly* internationally available 'off the shelf parts'

### User interface

- Alarms for loss of power, loss of breathing circuit integrity, high airway pressure and low battery life
- Display of settings and status
- Standard connection ports
- Button/Control Lock-out to protect accidental adjustment

### Repeatability

- Indicators within 10% of correct reading
- Breath frequency accurate to one breath per minute ( 1 out of approx 30 breaths )

## Posted by @Simon Kiersey on Slack (adapted from Medium article (need source)

- Be reliable. It must work continuously without failure (100% duty cycle) for blocks of 14days — 24 hours a day. If necessary, the machine may be replaced after each block of 14 days x 24 hours a day use.
- Provide at least two settings for volume of air/air O2 mix delivered per cycle/breath. These settings to be 450ml +/- 10ml per breath and 350ml +/- 10ml per breath.
- Provide this air/air O2 mix at a peak pressure of 350 mm H2O.
- Have the capability for patient supply pipework to remain pressurised at all times to 150mm H20.
- Have an adjustable rate of between 12 and 20 cycles/breaths per minute.
- Deliver at least 400ml of air/air 02 mix in no more than 1.5 seconds. The ability to change the rate at which air is pushed into the patient is desirable but not essential.
- Be built from O2 safe components to avoid the risk of fire and demonstrate avoidance of hot spots.
- Be capable of breathing for an unconscious patient who is unable to breathe for his or herself. Ability to sense when a patient is breathing, and support that breathing is desirable but not essential.
- Be able to supply pure air and air O2 mix at a range of concentrations including at least 50% and 100% Oxygen. Oxygen shortages are not expected, but the ability to attach a Commercial Off The Shelf (COTS) portable O2 concentrator machine may be a useful feature.
- Support connections for hospital Oxygen supplies — whether driven by piped or cylinder infrastructure (regardless, oxygen tubing is pretty standard, so an O2 fitting should be available)
- Be compatible with standard COTS catheter mount fittings (15mm Male 22mm Female)
- Fail SAFE, ideally generating a clear alarm on failure. Failure modes to be alarmed include (but are not limited to) pressure loss and O2 loss

## Later upgrades:
- Add redundancy to increase reliability.

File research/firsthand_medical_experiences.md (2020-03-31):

## Feedback I received from an engineer that is also a nurse:
"Being in the industry: It's not hard to ventilate a patient - in a pinch you use a big rubbery bulb. Nursing and medical students do it from time to time to help transport patients. It's terrifying for the first minute or two. During an epidemic you could probably get by with teams of volunteers or boy scouts or something.
The bigger limiting factor is the cuff that seals the endobronchial tube in the patient's airway. Those are tricky to manufacture, place, and maintain. You also need to manage the patient's sedation (because it's hard to have someone inflate your lungs when you're wide awake, barfing from the tube wedged in your throat being one of many problems). And you need to run the IV pumps that are required to maintain that sedation - just ask Michael Jackson - as well as hydrating and nourishing a patient with a tube stuck in their throat.
So there's an important political factor: Health care is largely a package deal, requiring skilled people."
---
## Clinical_Notes_OpenLung_March23_2020
### Submitted by: @leigh.ibis
The following is from a Montreal based Anesthesiologist (not me, I am just posting his email) . I am just getting used to this interface - feel free to email me (leigh.ibis@gmail.com) w/ questions so I see them and I shall try to get them answered by the clinical experts:

**I will describe what I see & comment accordingly; BMV= bag [face]mask ventilation on first glance this is a “bag squeezer” for “multiple unconscious victim environments” [natural disaster/conflict] I will assume the patient is intubated as a “facemask” must be secured to the victim [usually by a harness if not by hand] & can suffer leaks. I will not comment on the engineering elements e.g. mechanicals/power source etc however we do need to modulate the actuation of these mechanicals.

From a ventilation point of view, we need to modulate 4 variables;

FiO2 [fraction of inspired oxygen] room air is 21% oxygen = FiO2 0.21

Vt [Tidal volume of each breath] calculated as 4-6ml/kg ideal body weight

RR [respiratory rate] minimum of 10 breaths/minute

Ip/Ep [Inspiration & expiration pressure] max 40 mmHg / min 0 mmHg wrt to atmospheric

As a “bag squeezer” the FiO2 is reliably 1.0 [100% O2] only if there is a reservoir bag on the Ambubag [the bag that is being squeezed] attached at the supply end. This requires an oxygen supply with an integrated step down [Adams] valve as cylinder or wall supply is 4 bar

Vt is modulated by the amount by which the “bag” is squeezed; thus the motor winding the strap, squeezing the bag must be able to me modulated to wind the strap more/less depending on the observed chest excursions resulting from the movement of air. this could be simply a dial as we are not aiming for a measured Vt, rather an observed on in a “disaster” situation.

RR = frequency of the motor actuation, combined with speed of actuation will result in a longer or shorter inspiratory time... usually we divide 60 seconds by the time of each complete respiratory cycle to equate to the frequency of ventilation; just as an example motor actuated over 2 seconds [inspiratory time], release over 1 second, pause for 3 seconds; total respiratory cycle 6 seconds = ventilation frequency 10 cycles/minute. shortening the pause will increase the frequency of ventilation up to a maximum of 20 [i.e. zero pause time].

Inspiratory pressure must be limited to less than 40 mmHg to avoid lung injury [product of lung compliance and inspiratory time]. expiratory pressure must return to zero to avoid progressive inflation of the lungs [breath stacking] with sequential breaths.

These are universal properties & considerations for any type of ventilator. please let me know if this is what you were looking for?

NB expiratory gases in this design are vented to air through a Rubens [one way valve] at the patient end of the Ambubag thus CoVid aerosol contamination is a problem we need to acknowledge [unless scavenged]. If we are designing a CoVid ventilator [invasive or non-invasive] we will need to be able to adjust, measure & control all 4 of the above variables including be able to titrate the PEEP [positive end expiratory pressure] that is universally required in CoVid-19 ARDS [adult respiratory distress syndrome].

I hope all this helps!?**
---

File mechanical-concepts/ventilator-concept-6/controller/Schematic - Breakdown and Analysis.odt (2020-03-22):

Organization: Opensourceventilator.ie

Document: breakdown and analysis of electrical and software needs

Author(s): Paul McGowan, Steve Siebert, (add your name if you add content!)

Version: 1.0

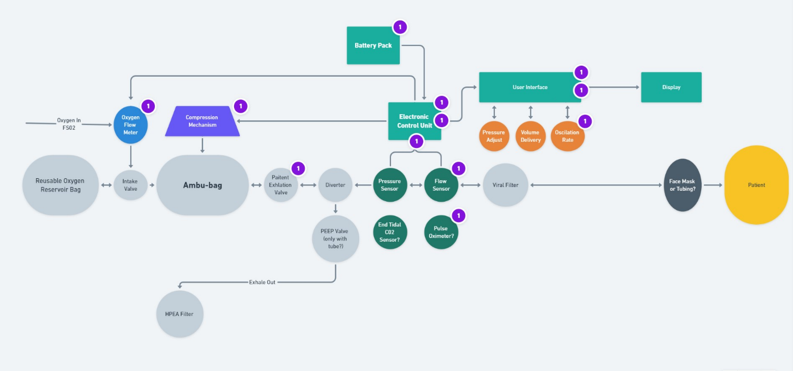
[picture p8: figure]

Purpose:

The purpose of this document is to break down the flowchart above into component parts and form a segmented specification for hardware and software. This information may then be distributed and the larger task of developing the system can be broken down and tackled by the plethora of talented volunteers on the project team Slack page. This is most definitely a work-in-progress.

Other sources:

In working on complicated projects, it is worthwhile to see how others have done / explain the same concepts. Here is an alternative diagram from https://www.slideshare.net/scribeofegypt/anatomy-of-the-ventilator – accessed March 20th, 2020.

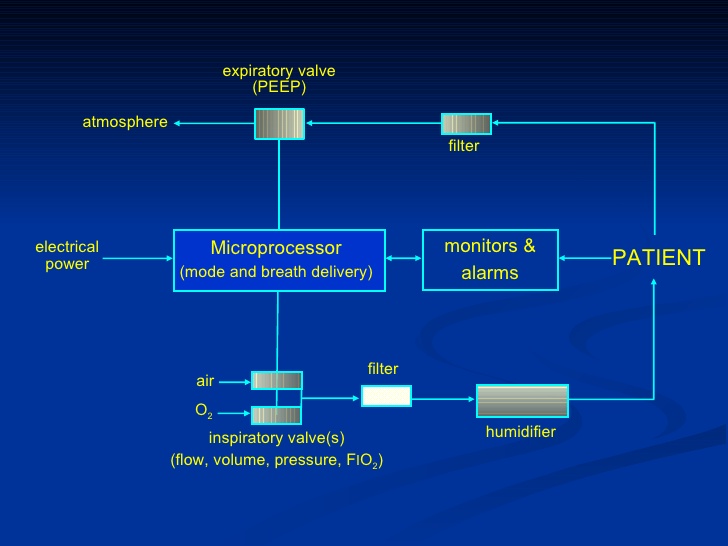
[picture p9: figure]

Oxygen flow meter:

The most common method of Oxygen flow metering, or mass flow metering, is a thermal flow meter. The basic principle is that the gas flow passes a filament and the temperature of the filament is related to the amount of Oxygen present. I believe it gets hotter as more oxygen passes. Example sensor:

https://www.digikey.com/product-detail/en/renesas-electronics-america-inc/FS1012-1100-NG/800-3790-ND/7645218

Compression mechanism:

This is the physical mechanism that squeezes the bag. Currently being prototyped (#6 and #7 as of March 20th, 2020), the consensus is a NEMA stepper motor, which will involve a pulsed DC drive of either unipolar or bipolar means at frequencies (estimated) <= 1kHz with (estimated) 10-50% duty cycle. The amount of current necessary per pulse is TBD.

Insert any other electrical specs or motor examples here.

Pressure sensor:

A pressure sensor, potentially a piezoelectric/diaphragm-type, is necessary to monitor pressure between apparatus and patient. Potentially digital or analog output. This is usually either a digital count between a minimum and maximum, or a conditioned analog output as a percentage of some maximum.

A digikey search honing in on a potential candidate:

https://www.digikey.com/products/en/sensors-transducers/pressure-sensors-transducers/512?k=pressure+sensor&k=&pkeyword=pressure+sensor&sv=0&pv1878=1211&pv1878=2087&pv1878=2171&pv1878=2406&pv1878=32407&pv1878=33119&pv1878=36058&pv1878=41594&pv1878=51779&pv1878=52273&pv1878=58520&pv1878=59969&pv1878=168620&pv1878=127644&pv1878=135508&pv1878=202501&pv1878=174935&pv1878=176796&pv1878=176936&pv1878=249096&pv1878=230290&pv1878=234537&pv1878=267210&pv1878=250771&pv1878=269078&pv1878=269197&pv1878=270753&pv1878=271035&pv1878=297914&pv1878=298341&pv1878=74299&sf=1&FV=1989%7C0%2C-8%7C512%2C218%7C307133%2C218%7C338588%2C218%7C338649%2C218%7C350336%2C218%7C400888%2C218%7C419488&quantity=&ColumnSort=1000011&page=1&stock=1&rohs=1&pageSize=25

Perhaps this component would be good as a start:

https://www.digikey.com/product-detail/en/omron-electronics-inc-emc-div/2SMPP-02/Z3059-ND/2504247

This OMRON component will need its analog output (0-31mV) to be scaled and filtered to meet the demands of a microcontroller ADC input.

Flow sensor:

Again, a flow sensor is needed and may be this device:

FS1012-1020-NG

However, as the flow rate may be affected by humidity, a humidity sensor may also be necessary to correct the readings. Propose to team and look into this.

Unified pressure and flow measurement scheme:

Using two MPXV7002 pressure sensors and a 3D printed laminar flow restrictor.

See https://docs.rs-online.com/02f9/0900766b814cade7.pdf

https://instrumentationtools.com/laminar-flow-meter-working-principle/

https://osventilator.slack.com/archives/C010GDV3LJC/p1584869593151200

Sensors can be mounted on control board and fed pressure from each side of the flow restrictor through non-clampable tubing. No wires required to go to flowmeter.

In order to avoid acoustic and electric noise, a high order digital LPF was proposed on the ADC inputs.

Electronic control unit:

There are a wide variety of available devices for use to fill this need. Below is a list of minimum specifications, keeping in mind all of the sensors that are necessary to support, the motor drive, the user interface, etc.

Motor drive:

Brute-force pulses into transistor drivers or gated pulse-width modulation may be the two main sources of stepper motor drive signaling. These signals may or may not need to be optically-isolated from the motor drive circuitry itself.

*Pulse-width modulation or precision timing capability for this purpose.

Flow sensors(2), pressure sensor (1), Oxygen pulse oximeter (1), End tidal CO2 sensors:

Though the exact configuration is not yet known, one can err on the side of caution and propose a minimum amount of capabilities:

*Between 5 and 10 ADC channel (10 bit minimum?); monitoring both sensor input, power supply levels, battery charge characteristics, and other yet unknown parameters

*(Synchronous) serial port capabilities; SPI, I2C, UART for debugging and/or networking capability (debug mode or normal mode?)

*General pulse I/O with interrupt-on-change capabilities for use with limit-switch sorts of I/O, user interface, LED indication, bit-banging for 7-segment display via shift registers, etc. etc.

*A second serial port for interfacing to a multi-channel DAC or one of several variable potentiometers for use in trimming/calibrating analog signal conditioning circuitry

*Quadrature encoder module or similar functionality to maintain the current position of the motor (note that if a stepper does not step, the pulse would be counted but the position would be unknown; care must be taken as to how we do this)

*CTMU or equivalent way to gather user “button presses”, however they may arrive and through whichever mechanical (or electrical) means decided upon

- IOC button presses? Cheap, needs hardware; pull-ups built-in, software filtering
- Capacitive touch pads on PCB? Cheap, needs software resources; timer and CTMU peripheral or external cap and current source
- Rotary encoder? Hardware and software resources, not as cheap, pull-ups built-in, software filtering, IOC CPU-intensive for short bursts
- Membrane switch? Cheap in mass quantity, needs hardware, pull-ups built-in, software filtering, may not last as long as other options

Capacitive sensing least ESD sensitive if board layout done properly, and hardware cheap (free copper!) but software resources and stability obviously a concern. Ways to deal with this, though.

I am personally familiar with 8-bit PICs; 18F4550, 16F877a, 16F1937, 12F683,...the list goes on. I see a device with no less than 44 pins, as a first guess, based on the list above. I/O can be expanded with 8-bit I2C expander ICs, and I2C with addressable devices; SPI with 1-of-8 decoder chips...will have to extrapolate and figure it out. MPLAB has automatically-generated drivers for their peripherals on most chips, and Microchip has plenty of following for support.

Arduino is naturally another popular contender, as is the ESP32 for its integrated IoT capabilities.

Steve Siebert and I are looking into those three options.

Display:

In this particular application, I think the local electronic control unit should have user diagnostic LEDs and/or a character LCD, along with a data output port to a more capable graphical LCD solution.

Whether this is a Rpi-zero, PC running linux, (whatever)pad with an app,...this is TBD. If I had to do something quickly, it would be C# form app using their chart control for easily-generated and controlled line strip charts. I have run C# via wine on raspian with ease in the past. However, others will know the more convenient and efficient method of solving this problem. Please add info here!

Overall thoughts on architecture of the system:

The want and/or need of an IoT-capable system has been expressed by Steve Siebert and myself, and we envisioned at this time single self-contained electronic systems that have the capability of publishing results via request from a main hub, or via asynchronous means to conserve battery life on portable units. In either case, he has some ideas he is working on and perhaps he can elaborate here.

Battery power:

For portable applications, an efficient solution would allow battery power to be utilized. Though the time constraint is not yet known (to me), perhaps a good rule-of-thumb to start is a 5 hour trip in an ambulance or other transportation to a hospital.

Steve and I discussed battery technology; in the interest of time, SLA (sealed lead-acid) battery technology is a bit heavy and antiquated, but the charge circuitry is very straightforward and these batteries are available practically everywhere. A 5-10 AH battery @ 12V may be plenty for the 50% duty cycle (estimate) motor needs and electronic control subsystem(s). Potential connection to solar panel might become a need as well; although I have not seen this come up thus far. I imagine that, in the interest of the application, we would prefer to stick to 24V and below to protect the user and to keep with commonly-available boost and buck regulators, should we need them. Stepping 12 VDC to 24 VDC for low duty cycle motor drive is not too big a task, but 12 VDC to 60VDC+ introduces new issues and inefficiencies without quality parts and lots of thought.

TODO:

More information on which sensors, what interfaces, mounting, constraints, costs

More information on “how big the box” is, user interface, power consumption

More information on power requirements, lifetime on battery, battery tech, etc.

More information on motor specifications and position sensing

More information on overall system architecture

etc etc.

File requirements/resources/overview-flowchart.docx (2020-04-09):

OpenLung
Medical
Mechanical
User-Specified Button
breath/min (Via button or knob interface)
insp./exp ratio, tidal volume
Assist Control
Negative Pressure Detection?
Positive end-expiratory pressure (PEEP)
Maximum pressure limiting
Humidity exchange
Built into the mask
Infection control
By way of covering the unit in an easily cleaned enclosure
Limited dead-space
Economic
User Interface
Repeatability
Portable / Stationary
stationary design will be a seperate branch?
index on stationary? - The Rice/MIT designs are for dev world. This project assumes use in a resource limited hospital
Standalone operation
Reaching full autonomy is beyond the scope - the target should be that this is managable with a 1:4 RN:PT ratio
Robust mechanical, electrical and software systems
Readily sourced and repairable parts
Minimal power req Efficient motor controller
Full autonomy by way of sensor feedback and adjustment loops
Simple, Corrosion resistant, Vibration resistant, Best crystal oscillator
3D printing
Low Cost
$100.00 usd build cost
Must fit within standard printer bed
target stamping. The US/Canada has hundreds of stamping shops that can producer stronger parts in faster volumes than 3D printing. large enough 3D printers for this are limited, and slow in production. A single stamping shop can make 100s of these a day
Must use internationally available 'off the shelf parts'
Alarms
for loss of power,
loss of breathing circuitintegrity,
high airway pressure
low battery life
Display
settings and status
Standard connection ports
Indicators within 10% of correct reading
Breath frequency accurate to one breath per minute ( 1 out of approx 30 breaths )

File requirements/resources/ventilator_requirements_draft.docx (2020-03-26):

Edit this here: https://docs.google.com/document/d/1h77FkKXqPOwVqfOj-PIJSjYX9QiEx69Av2gYuzqZolw/edit?usp=sharing

# COVID-19 ARDS Ventilator

ARDS - acute respiratory distress syndrome

From https://www.propublica.org/article/a-medical-worker-describes--terrifying-lung-failure-from-covid19-even-in-his-young-patients

“It’s called acute respiratory distress syndrome, ARDS. That means the lungs are filled with fluid. And it’s notable for the way the X-ray looks: The entire lung is basically whited out from fluid. Patients with ARDS are extremely difficult to oxygenate. It has a really high mortality rate, about 40%. The way to manage it is to put a patient on a ventilator. The additional pressure helps the oxygen go into the bloodstream.”

“With our coronavirus patients, once they’re on ventilators, most need about the highest settings that we can do. About 90% oxygen, and 16 of PEEP, positive end-expiratory pressure, which keeps the lung inflated. This is nearly as high as I’ve ever seen. The level we’re at means we are running out of options.

“In my experience, this severity of ARDS is usually more typical of someone who has a near drowning experience — they have a bunch of dirty water in their lungs — or people who inhale caustic gas. Especially for it to have such an acute onset like that. I’ve never seen a microorganism or an infectious process cause such acute damage to the lungs so rapidly. That was what really shocked me.”

Medtronic (and others) design and build the ‘Ferrari’ of ventilators, OSVentilator Project intends on designing and building a ‘bicycle’

# Scope

Develop a low-cost, open source ventilator for emergency use to provide ventilation for COVID-19 ARDS patients that have no access to existing ventilators due to overwhelming demand on the medical system of any given country.

All mechanical elements ‘in the patient airway’ must be medically approved. Control electronics and software must be developed in line with existing medical device standards.

People will die if this device doesn’t operate correctly

All design documents - mechanical, electronic and software - will be made freely available via the Open-Source-Ventilator (OSV) project here: https://gitlab.com/open-source-ventilator/OpenLung

## Indication

The OSV device is indicated:

1. As an accessory to a bag valve mask
2. For patients in an acute emergency during complications of COVID-19
3. Patients will most commonly be experiencing acute respiratory distress (ARDs), they may or may not be spontaneously breathing and they are likely ventilator dependent.

## Environments of use

AN OSV device can be used in three different environments.

1. Acute Hospital Environment
2. Ambulatory scenario within the hospital
3. Transport situation (e.g. ambulance)

# Mechanical ventilator minimum specifications

Three common modes of control in Ventilators:

1. Volume Control
2. Pressure Control
3. Pressure Regulated Volume Control (PRVC)

Minute Ventilation (MV) = Tidal Volume (VT) x Respiratory Rate (RR)

MV = amount of air a patient moves in a minute

MV can be 5 - 10 lpm in a normal patient but can be 30lpm in a sick patient

FS02 - Flow (source) O2. The flow from the supply.

FDO2 - Flow (delivered) O2. The flow of O2 at the patient mask.

FiO2 - Flow (inspired) O2. The O2 in the patient.

Balloon

Ambu bag (BVM)

Pressure

Tubing

PEEP

Flow

HEPA

Patient

O2

Valve

uC

Alarm

Display

Battery

PSU

Keys

Motor

Exhaled Air

Fig. 1: System overview

These appear to be the accepted ranges for treating Convid-19 ARDS - from UCC’s ARDS Ventilatory Management PDF:

Variable | Range | Accuracy | Settings | Default | Notes
Tidal Volume (VT) | 4-6ml/Kg IBW* (205 - 530ml) | ±0.5ml | ±1ml/Kg (35ml) | -
Respiratory rate (RR) | 15-35bpm | ±2bpm | ±2bpm | 15bpm
I:E Ratio | 1:1 - 1:5 | ±0.5 | 0.5 | 1:1
Plateau Airway Pressure (PAW) | 10-30cmH2O | ±1cmH2O | ±1cmH2O | < 30cmH2O | If > 35 VT needs to be decreased to 5 or 4ml/Kg IBW
Driving Pressure (PAW-PEEP) | 5-25cmH2O | - | - | | Not directly adjustable. Set by PEEP and / or PAW
PEEP | 5-24cmH2O | ±1 | ±1 | 5cmH2O | Manual controls are fine. Pressure sensor will sense this and can be displayed.

(*)Calculate Ideal Body Weight (IBW, Kg) using patient height (cm):

Male | Female
= 50+0.91x(height in cm-152.4) | = 45.5+0.91x(height in cm-152.4)

## Humidification

Not in scope. This could be considered a ‘comfort feature’ for long-term use.

## Nebulizer

Not in scope. Nebulizers are used to deliver inhaled prostacyclin analogues in patients with severe ARDS and refractory hypoxemia. See ISO/AWI 27427 for connector specs.

## Mask & Intubation

Depends on patient’s clinical condition. Non-invasive mask or helmet ventilation is typically used if the patient is alert, reasonably stable and the main problem is severe hypoxemia and the lungs are not too stiff. Endotracheal intubation is generally required if the patient is too agitated to wear mask, is exhausted, has decreased level of consciousness or is profoundly hypoxemic (low level of oxygen in arterial blood).

## Ventilator Modes

Control variable:

1. Volume control (VC)
2. Pressure control (PC)

Breath sequence:

1. Continuous mandatory ventilation (VC-CMV or PC-CMV)
2. Intermittent mandatory ventilation (VC-IMV, PC-IMV)
3. Continuous spontaneous ventilation (CSV)

Triggering:

1. Patient triggered via pressure drop

From http://rc.rcjournal.com/content/56/1/52

## Cycling of the Mechanical Ventilator Breath

The change from inspiration to expiration is a crucial point in the mechanically ventilated breath, and is termed "cycling".

Cycling Mechanisms:

- Pressure (PMAX - I’m using this for want of a better term ~ there may be a standard term used here)
  - When a set pressure is reached, inspiration is cycled into exhalation. Most commonly used during alarm - if a patient becomes extremely asynchronous (in their breathing) or coughs, a high-pressure alarm may be triggered and the inspiration phase will end.
- Time (TCY)
  - Switch from inspiration to exhalation when a set time period is reached. This can be achieved by setting the Resp Rate, Inspiratory Time or I:E Ratio. Many ventilators terminate the inspiratory phase after 3-5 secs.
- Volume (VT & VTMAX)
  - Inspiration stops once VT is reached. Cycling to exhalation phase will occur when VT OR VTMAX is reached.
- Flow (FCY)
  - During pressure-support ventilation (PSV), the patient both triggers and cycles the breath. (See diagram below) When a patient's inspiratory flow decreases to 25% of peak inspiratory flow, the breath would cycle to the exhalation phase.

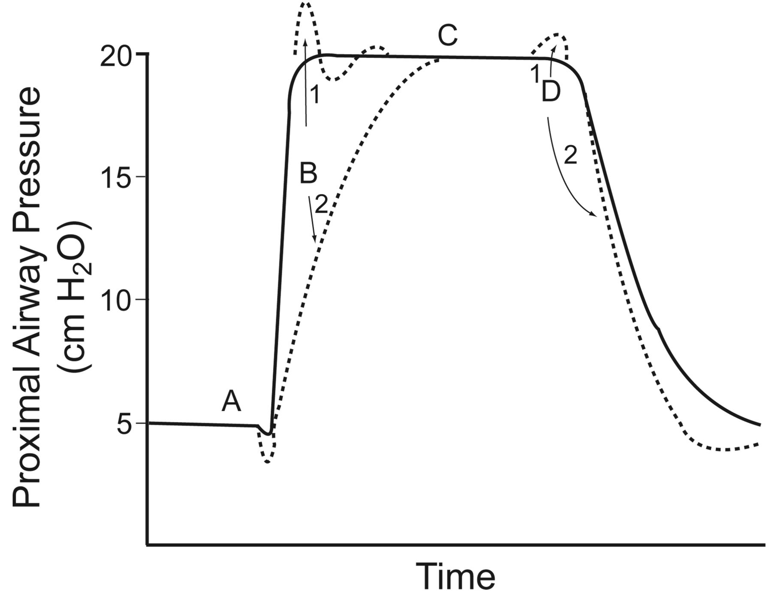
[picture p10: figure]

Characteristics of a pressure-supported breath. In this example, the baseline pressure (ie, PEEP) is set at 5 cm H2O, and the pressure support is set at 15 cm H2O. The inspiratory pressure is triggered at point A by a patient effort, resulting in an airway pressure decrease. The rise to pressure (line B) is provided by the initial flow into the airway. If the initial flow is excessive, the initial pressure exceeds the set level (B1). If the initial flow is low, there is a slow rise to pressure (B2). The plateau of pressure support (line C) is maintained by control of flow. A smooth plateau indicates appropriate flow responsiveness to patient demand. Termination of pressure support occurs at point D and should coincide with the end of neural inspiration. If breath termination is delayed, the patient may actively exhale (the pressure rises above the plateau) (D1). If breath termination is premature, the patient may have continued inspiratory efforts (D2). (Adapted from Reference 18, with permission.)

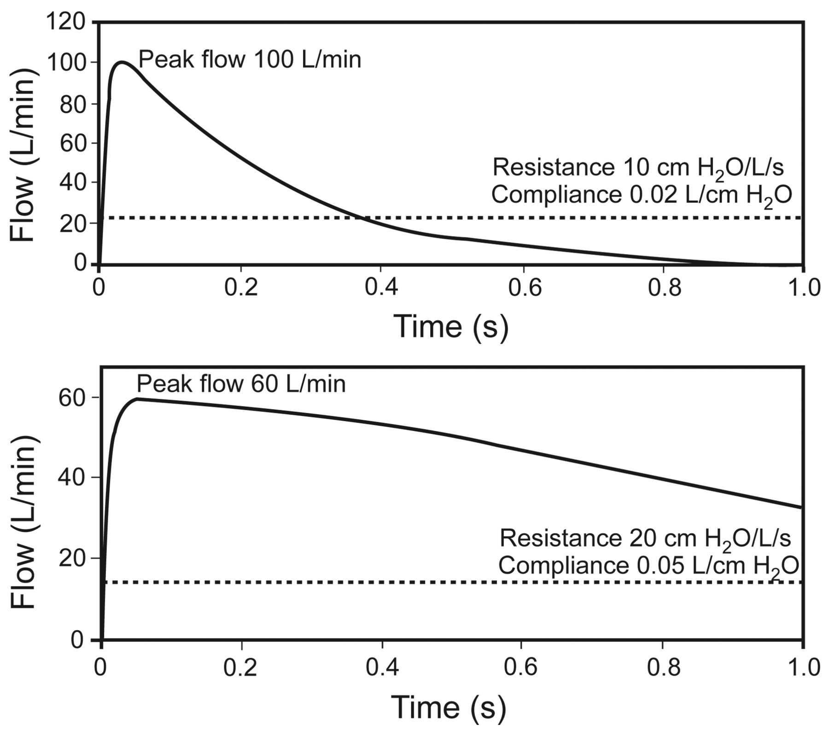
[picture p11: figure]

Effect of respiratory mechanics on cycling of pressure support from inhalation to exhalation. Flow cycling is set at 25% of the peak flow, as illustrated by the broken line. The upper panel represents the respiratory mechanics of a patient with restrictive lung disease. The lower panel represents the respiratory mechanics of a patient with obstructive lung disease. In each case the neural inspiratory time is 1.0 second. The breath terminates prematurely in the patient with restrictive lung disease, but the breath is prolonged in the patient with obstructive lung disease. Also note that the peak flow is greater in restrictive lung disease, and the pressure decrease is more rapid in restrictive lung disease. (Adapted from Reference 19.)

# Alarms

There must be a visual display of an alarm situation. This must be visible from XXm.

There must be an audio alarm, with continuous sound of YYdB.

Alarms may be silenced, for a period of ZZ seconds, via the user interface. If the underlying alarm condition has not been cleared, the alarm will sound again.

There are 3 types of alarms:

1. Input - power supply and air / oxygen source
2. Control - incorrect settings of control variables
3. Output - incorrect outputs from the Ventilator to the patient

Alarm type | Min | Max
Minute Ventilation (MV) | 5lpm | 30lpm
Peak Pressure | | 60cmH2O
Low Pressure | 5cmH2O
Tidal Volume (VT) | <200ml | >600ml
Input Power
Battery SOC | <50%?? | Reset alarm >90%SOC
Failed Self Test

## Sensors & Control Valves

1. PEEP - Adjustable between 5-16cmH2O. Need to source a PEEP valve.
2. SpO2 - can we get this from an external, existing hospital sensor?
3. FSO2 / FDO2 / FiO2??? - O2 sensors? Need medical ones?
4. O2 flow - valve???
5. Flow - Sensirion SFM3300 or similar (I2C interface)
6. Pressure - ??? Can we measure this outside of the ‘patient airway’?
7. Accuracy???
8. Max pressure valve of 40 cmH2O - ensure pressure delivered to patient cannot exceed this level.

## Power Supply

Mains power. Medical grade PSU ideally operating on universal input - 90V - 240V AC, 50 - 60Hz, with an output of XX V DC, @ YY Amps.

Battery backup. A cheap, reliable, widely available battery providing power to the entire system for 60 mins. Battery should recharge once mains power is returned. Battery should recharge from 50%SOC to %90 SOC within 60 mins.

## User Interface

What must be displayed?

What is the minimum?

1. Resp. rate
2. Pressure
  a. PEEP
  b. Peak
3. Flow
4. Tidal Volume
5. Therapy
  a. ??

What’s nice to have?

1. O2 sat.
2. Spontaneous vs delivered breath

Method of interacting with display. Buttons or rotary encoder.

## Self Tests

Battery. Test battery is operational and can power the entire device.

Sensors. Perform built-in self test on all sensors.

Motors. Ensure motors are operational and moving within set limits.

Microcontroller. Tests?

## Safety

Fire? Wiring?

Fail-safe - motors? Valves fail open/closed?

Max. pressure release valve fixed at 45cmH20

Asphyxia valve set at 5cmH20???

HEPA filters

## Environmental

Operating Temperature: 5℃ to 40℃

Transport / Storage Temperature: 0℃ to 60℃

Operating Humidity: 15% to 93%

Operating Altitude: -170 to 4877m

## Mechanical

Widely available materials

Easy clean surfaces that are not affected by hospital cleaning products??

## Cost

Bill of Materials < $YYY or €XXX

## Ventilator Standards

Standards relating to ventilator use, operations and design:

1. ASTM F 1100-90 (Standard Specifications for Ventilators Intended for Use in Critical Care) (Withdrawn without replacement in 2004)
2. ASTM F 1246-91 (Standard Specification for Electrically Powered Home Care Ventilators, Part 1-Positive-Pressure Ventilators and Ventilator Circuits) (LINK (https://civilengineersstandard.com/wp-content/uploads/2019/02/F-1246.pdf))
3. IEC 6061-2-12(Standard for Critical Care Ventilators)
4. IEC 62304 (Software Design for Medical Devices, presumed Level C)
5. ISO 80601-2-12:2020 Medical electrical equipment — Part 2-12: Particular requirements for basic safety and essential performance of critical care ventilators
6. ICS 11.040.10 (ANAESTHETIC, RESPIRATORY AND REANIMATION EQUIPMENT INCLUDING MEDICAL GAS INSTALLATIONS)
7. ISO 10651-3:1997 (Lung ventilators for medical use — Part 3: Particular requirements for emergency and transport ventilators)
8. ISO 10651-4:2002 (Lung ventilators — Part 4: Particular requirements for operator-powered resuscitators)
9. ISO 10651-5:2006 (Lung ventilators for medical use — Particular requirements for basic safety and essential performance — Part 5: Gas-powered emergency resuscitators)
10. ISO 19223:2019 (Lung ventilators and related equipment — Vocabulary and semantics)
11. ISO/TR 21954:2018 (Guidance on the selection of the appropriate means of ventilation based on the intended patient, use environment, and operator)
12. ISO 80601-2-72:2015 Medical electrical equipment — Part 2-72: Particular requirements for basic safety and essential performance of home healthcare environment ventilators for ventilator-dependent patients
13. ISO 80601-2-79:2018 Medical electrical equipment — Part 2-79: Particular requirements for basic safety and essential performance of ventilatory support equipment for ventilatory impairment
14. ISO 80601-2-80:2018 Medical electrical equipment — Part 2-80: Particular requirements for basic safety and essential performance of ventilatory support equipment for ventilatory insufficiency
15. ISO/DIS 80601-2-87 (Medical electrical equipment — Part 2-87: Particular requirements for basic safety and essential performance of high-frequency ventilators)
16. ISO/FDIS 80601-2-84 (Medical electrical equipment — Part 2-84: Particular requirements for basic safety and essential performance of ventilators for the emergency medical services environment)
17. BSEN 794-3:1998 +A2:2009 Particular requirements for emergency and transport ventilators

Connectors for Respiratory Devices:

1. ISO/AWI 27427 Nebulizing systems and components (Under Development)
2. ISO/AWI TR 22175 Connectors for respiratory devices (Under Development)

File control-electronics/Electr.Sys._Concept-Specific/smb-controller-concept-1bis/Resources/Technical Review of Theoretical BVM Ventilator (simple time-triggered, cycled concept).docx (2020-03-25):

# TECHNICAL REVIEW:

# Theoretical Bag Valve Mask Ventilator

# 1 Terms and Definitions

Alveolar space – The region of the respiratory system that is composed of elastic, gas-permeable tissue that exchanges gas with the circulatory system.

Airways – The region of the respiratory system that carries gas from the mouth/nose to the alveolar space but does not participate in gas exchange.

Inspiratory time fraction – The portion of the breath time that is provided for inspiration.

Instrumental dead space – The volume of all the breathing system components that carry both inspiratory and expiratory gas.

Peak inspiratory pressure – The maximum airway pressure that occurs during an inspiratory cycle.

Respiratory rate – The number of breaths delivered per unit time.

Tidal volume – The volume inspired or expired in a single breath.

Term | Definition
BVM | Bag valve mask
CO2 | Carbon dioxide
FDA | Food and Drug Administration
O2 | Oxygen

# 2 Theoretical Device Background

The most common manually operated breathing assistance device is the bag mask valve (BVM) which requires manual articulation and the full attention of a medical worker to ensure consistent operation. Additionally, owing to their manual nature, delivery of consistent ventilation is difficult with such devices. The theoretical device would aim to overcome these limitations by providing an automated assisted breathing device that is more accessible than current options and will free medical staff to perform other life-saving tasks. The theoretical device may or may not look something like the following (CRITICAL NOTE: THE PROPOSED THEORETICAL DEVICE WOULD COMPRESS/EXPAND THE BAG BASED ON TIMING ONLY, NOT SENSORS, WHICH EXPLAINS CERTAIN LIMITATIONS DESCRIBED BELOW):

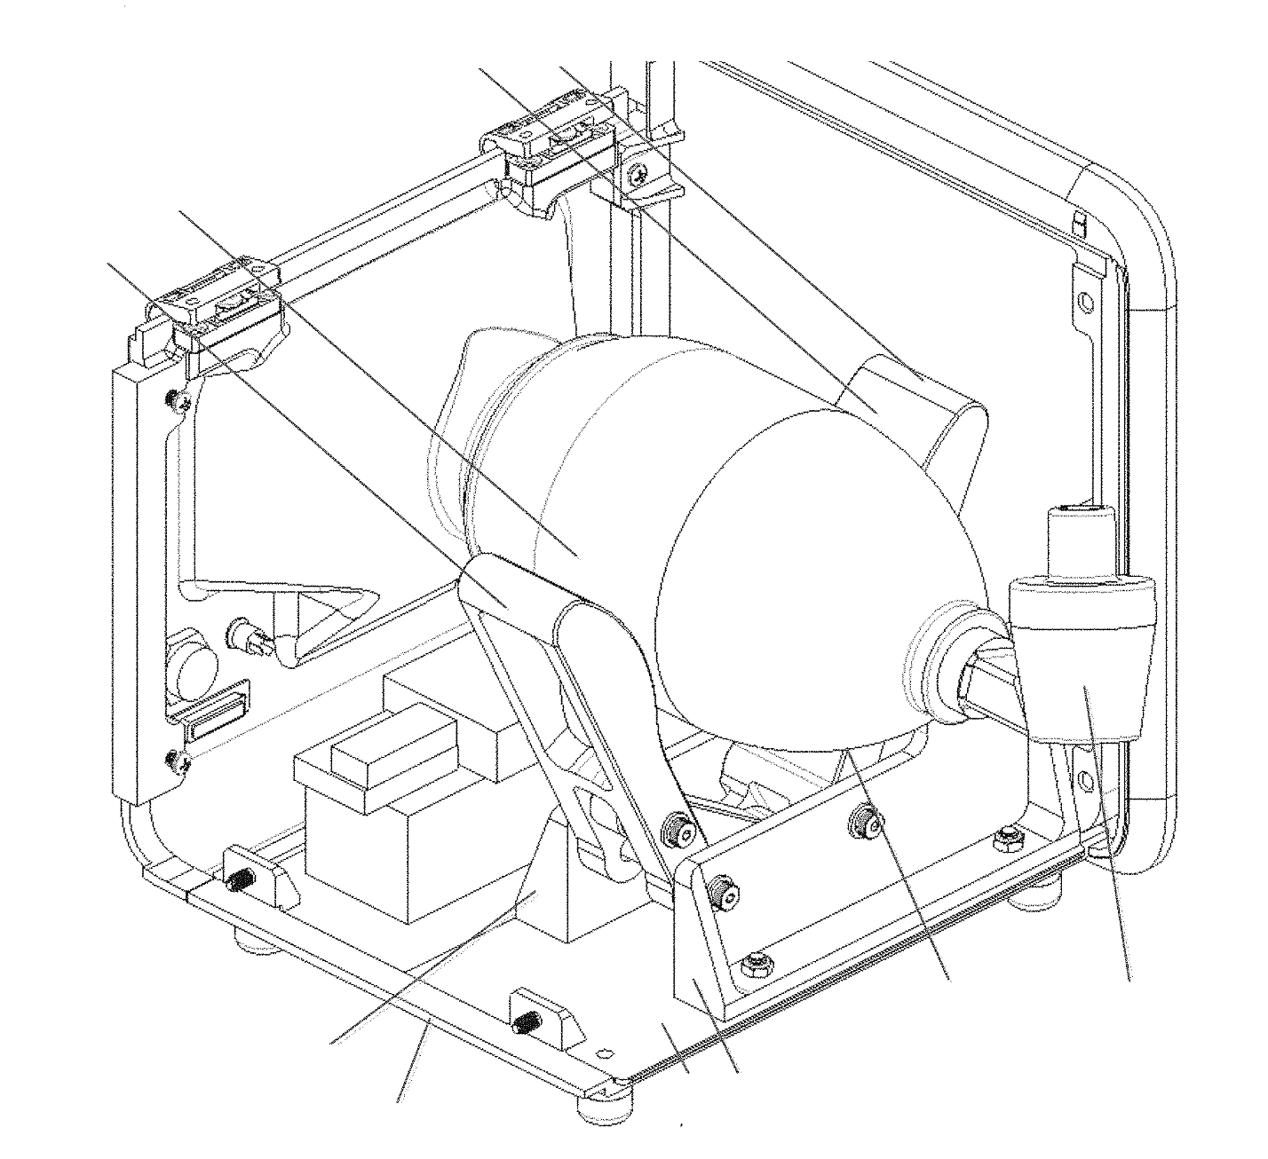
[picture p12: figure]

The target market for this product will be hospitals and medical institutions, particularly in resource limited settings. Additionally, if it is relatively compact and internally powered, the potential product will also be usable in emergency response and during patient transport.

# 3 Key Relevant Standards

The following list represents a selection of key standards that should be reviewed and understood during early product development to help guide the design of the theoretical device. This list, however, is not exhaustive, and compliance with additional standards may be required for regulatory clearance that are either applicable to the specific design, features, or intended use of the product or to medical device development in general.

- IEC 60601-1 – Medical electrical equipment - Part 1: General requirements for basic safety and essential performance.
- IEC 60601-1-2 – Medical electrical equipment - Part 1-2: General requirements for basic safety and essential performance - Collateral Standard: Electromagnetic disturbances - Requirements and tests.
- IEC 60601-1-8 – Medical electrical equipment -- Part 1-8: General requirements for basic safety and essential performance -- Collateral standard: General requirements, tests and guidance for alarm systems in medical electrical equipment and medical electrical systems.
- EN 794-3 – Lung ventilators. Particular requirements for emergency and transport ventilators.
- ISO 10993-1 – Biological evaluation of medical devices -- Part 1: Evaluation and testing within a risk management process.
- IEC 62133 – Secondary cells and batteries containing alkaline or other non-acid electrolytes – Safety requirements for portable sealed secondary cells, and for batteries made from them, for use in portable applications.
- IEC 62304 – Medical device software -- Software life cycle processes.
- IEC 62366-1 – Medical devices -- Part 1: Application of usability engineering to medical devices.

# 4 Technical Review of Limitations of Simple Approach

## 4.1 Bag Valve Mask Overview

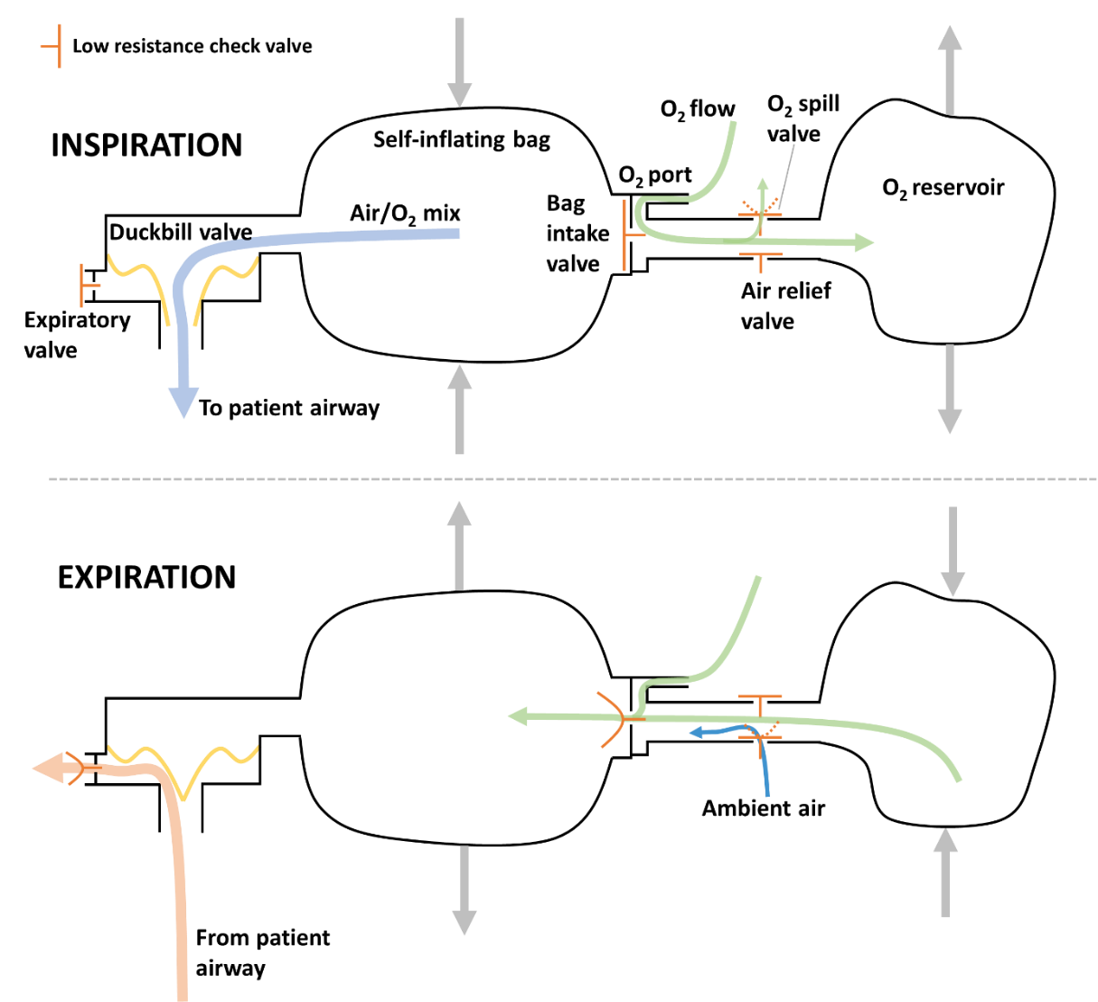
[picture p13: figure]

Figure 1: Schematic representation of a BVM

Figure 1 shows a schematic representation of a typical BVM. During inspiration, the self-inflating bag is compressed, generating a positive internal pressure. The positive pressure forces the bag intake valve closed and deforms the flaps of the duckbill valve to allow delivery of gas to the patient while simultaneously sealing the expiratory port/valve. Low pressure oxygen (O2) delivered through the O2 port is collected in an O2 reservoir; if the reservoir reaches capacity, excess O2 is released through the O2 spill valve.

During expiration, the self-inflating bag recoils to its uncompressed shape, generating a negative internal pressure. The negative pressure pulls the duckbill valve closed and draws O2 into the bag from the O2 reservoir. If the O2 reservoir is emptied, ambient air is entrained via the air relief valve. An annotated photograph of a commercially available BVM is shown in Figure 2.

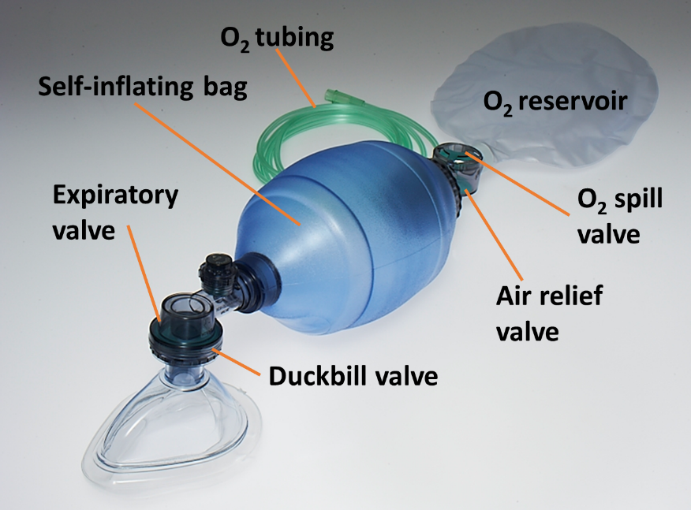
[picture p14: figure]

Figure 2: Commercially available BVM

## 4.2 Dead Space

The role of the respiratory system is to deliver O2 to, and eliminate carbon dioxide (CO2) from, the circulatory system. In the simplest representation, the respiratory system consists of the airways and alveolar space (Figure 3, bottom). During inhalation, fresh gas containing high O2 and no CO2 is drawn, via the airways, into the alveolar space. The alveolar space is composed of highly gas-permeable tissue that is in close communication with the circulatory system. In this space, O2 diffuses from the lungs into the blood and CO2 from the blood into the lungs. During expiration, the low-O2, high-CO2 gas is expelled from the alveolar space via the airways.

The instrumental dead space of a breathing system is the combined volume of all the breathing circuit components that carry both inspiratory and expiratory gas. As shown in Figure 3, any gas that is expired into the dead space of the circuit is subsequently re-inspired without being replaced with fresh inspiratory gas. Over multiple respiratory cycles, the dead space gas is continually depleted of O2, while the CO2 content continually rises. The physiological consequences of the instrumental dead space depend on its size relative to the tidal volume; in the worst case, no fresh gas reaches the alveoli.

For the theoretical device, all the tubing connecting the outlet of the BVM to the patient airway is dead space. Most ventilator systems are set up with approximately 2 m of tubing with 22 mm internal diameter between the ventilator and the patient to facilitate convenient placement of the ventilator and provide a low resistance path for respiration. If this length of tubing was used with the theoretical device, it would contribute 760 ml of dead space to the system. This is well above the average adult tidal volume of 500 ml and, as a result, this configuration of the device would be unable to support life for most patients.

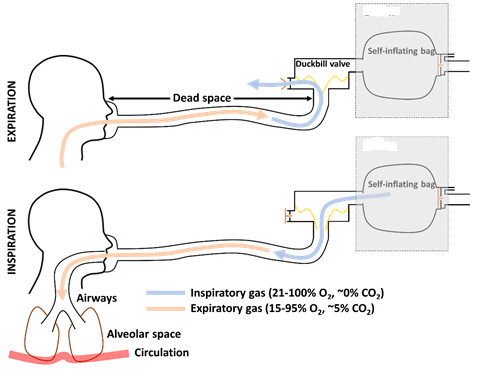
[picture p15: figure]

Figure 3: Theoretical device dead space

In general, it is advisable to limit instrumental dead space to less than 10 ml in adult patients and 5 ml for pediatrics. To maintain the overall “BVM in a box” concept and achieve this significant reduction in dead space, the duckbill/expiratory valve would have to be removed from the BVM and located at the patient airway (Figure 4). In our experience at IPD, this valve is not easily removable from most commercially available BVMs.

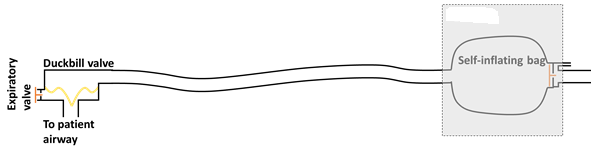
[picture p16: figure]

Figure 4: Theoretical device with reduced dead space

## 4.3 Uncompensated Compliance

When delivering positive pressure ventilation, in any inspiratory cycle, the total volume of gas that enters the lungs is always less than the volume of gas that exits the ventilator. This is a result of two related properties of the system – the compressibility of gas and the compliance of the breathing circuit.

As gas exits the ventilator, and pressure within the system rises, the spacing between gas molecules decreases so that more gas molecules are stored per unit space. At the same time, the increase in pressure causes the ventilator tubing and other parts of the breathing circuit to expand and accommodate more gas compared to the start of inspiration. This gas, which doesn’t reach the patient, is commonly referred to as “lost” to the compliance of the system.

For the theoretical device specifically, the patient tidal volume will be lower than the volumetric compression of the BVM. This effect may be compounded by the significant volume and elastance of the self-inflating bag. As noted in section 4.2, the volume of 2 m of standard ventilator tubing is approximately 760 ml. As the volume of a typical adult BVM is 1500 ml, the total theoretical device breathing system volume is approximately 2260 ml. Similarly, the volumetric expansion of 22 mm ventilator tubing is approximately 0.5 ml/cmH2O/m⁸. Based on a conservative estimate for the BVM compliance of 0.5 ml/cmH2O, the total circuit compliance can be approximated as 1.5 ml/cmH2O.

The gas lost to the system can be calculated according to Equation 1, where VL is the lost volume, and PIP, Patm, VC, and Cc are the peak inspiratory pressure, atmospheric pressure, breathing circuit volume, and breathing circuit compliance, respectively. Using the above approximations for circuit volume and compliance, the percent error in volume delivery can been calculated for a standard adult and pediatric patient⁹ (Table 1).

V_L =((PIP+P_(atm))/(P_(atm))-1)V_C +PIP∙C_c Equation (1)

Table 1: Volumetric error due to circuit compliance

Parameter | Adult | Pediatric
Static lung compliance (ml/cmH2O) | 50 | 20
Airway resistance (cmH2O/L/s) | 5 | 20
Set tidal volume (ml) | 500 | 300
Respiratory rate (breaths/min) | 10 | 20
Inspiratory time fraction | 0.33 | 0.33
PIP (cmH2O) | 11.3 | 21.1
Lost volume (ml) | 41.5 | 77.7
Delivered tidal volume (mL) | 458.5 | 222.3
Error: Delivered vs Target (%) | 8.3 | 25.9

Note: Patm of 1 atm was used in the above calculations

A priori compensation for this error is difficult to implement because, as shown in Table 1, the error depends on the delivered respiratory profile and the respiratory mechanics of the patient. In addition, the error will vary with the volume and compliance of the breathing circuit that is used, which may change between patients. Lastly, the compliance of an individual breathing circuit may change with temperature and over time.

This limitation is overcome in existing ventilators by a number of different techniques. Most commonly, ventilators execute a circuit compliance check before each new patient and then dynamically measure the circuit pressure and correct the delivered volume in real-time throughout inspiration. Other ventilators may incorporate a flow sensor at the patient airway for monitoring the actual delivered tidal volume. Alternatively, most ventilators implement a pressure control mode wherein the ventilator targets a specific airway pressure instead of a tidal volume, and the control loop inherently compensates for any volumetric losses.

## 4.4 Oxygen Delivery

As shown in Figure 1 and Figure 2, BVMs typically incorporate an O2 reservoir to collect O2 during compression of the self-inflating bag which is subsequently drawn into the system as the bag recoils. To achieve >95% O2 in the inspired gas⁹ the O2 reservoir should be large enough to accumulate at least one tidal volume. A bag of roughly 1 L should be sufficient for most patients. Based on IPD’s current understanding and review, the theoretical device does not contemplate the attachment of an O2 reservoir and associated relief valves. While provision of O2 without a reservoir will increase the inspired O2 fraction, the utilization of the supplied O2 will be inferior to the reservoir approach. For example, using a standard adult patient with a tidal volume of 500 ml, respiratory rate of 10 breaths/min, and inspiratory time fraction of 0.33, a flow of 5 L/min of O2 would result in ~100% inspired oxygen fraction with a reservoir; without a reservoir, the inspired oxygen fraction would be 73%. Addition of an O2 reservoir to the current design would require that the reservoir be placed externally, and a means provided to prevent unintentional compression (ex. a cage). Alternatively, the reservoir could be incorporated inside the theoretical device but would likely require an increase in product size to accommodate the additional volume.

## 4.5 Respiratory Rate

The respiratory rate achievable with the theoretical device will be limited by the rate at which the self-inflating bag re-inflates after compression. Although adult respiratory rates (~10 breaths/min) may be easily achievable, pediatric respiratory rates (20+ breaths/min) may be difficult to achieve with an adult sized bag. In normal practise, BVMs are available in various sizes to accommodate adults, pediatrics, and neonates, where the recoil rate of each type of bag is sufficient to achieve the respiratory rates required for the intended patient population. The theoretical device may contemplate the addition of loops and hooks to the bag/compression system to allow for pulling the bag during expiration. Although this solution is viable, it would require a custom BVM to implement.

## 4.6 Variations in Bag Valve Masks

The size and shape of BVMs is not standardized between products. If the theoretical product volume delivery is calibrated to a particular BVM, substitution of the BVM with a product with different geometry could lead to very significant errors in volume delivery. Additionally, the theoretical device structure would need to accommodate BVMs of varying shapes and sizes.

# 5 Considerations for Addressing Limitations

## 5.1 Parameters, Features, and Modes

Although the adjustable parameters, features, and available modes of ventilation differ significantly between ventilators, there is a subset of functionality that is common to many ventilators, including emergency and transport ventilators. The following is a list of some common functions that may be difficult to implement on the proposed theoretical device:

Inspiratory/expiratory timing – Although the theoretical device can vary respiratory rate based on the motor speed, it may be desirable to adjust the portion of the breath time that is allocated to inspiration and expiration separately. This would require sensing and feedback of the position of the compression mechanism to determine when the self-inflating back is being compressed (inspiration) and expanded (expiration), and adjustment of the motor speed during each phase appropriately. If this is not feasible, it is recommended that the device implement the most common inspiratory time to expiratory time ratio of 1:2, respectively. In general, it is unnecessary to control the rate at which the bag re-inflates and may be preferable to have the compression mechanism retract as quickly as possible after inspiration is complete.

Triggering/cycling – Triggering and cycling refer to the criteria for initiating and stopping inspiration, respectively¹⁰. The current concept of the theoretical device is both time-triggered and time-cycled. In many cases, it is beneficial to trigger or cycle a breath based on a patient signal. For example, patients do not always require full ventilatory support and may make weak and/or intermittent efforts to breath spontaneously. In this case, the ventilator may support spontaneous inspiratory efforts by detecting negative airway pressures and triggering a ventilator assisted breath. Similarly, a very high airway pressure during inspiration may indicate that the patient is trying to expire against the ventilator and the breath should be cycled. With the simple theoretical device, the motion of the compression mechanism is fixed. Implementation of any trigger or cycle conditions other than time may be very difficult as these features generally require near instantaneous switching between inspiration and expiration.

Pressure controlled ventilation – Most modern ventilators include a pressure control mode wherein the ventilator delivers a specific airway pressure profile instead of delivering a set tidal volume. Pressure control has many advantages over volume control, including automatic compensation for volume loss (compliance, leaks, etc.) and adjustment to changes in the patient’s respiratory mechanics. This mode, however, generally requires that the airway pressure be sensed and fed back to the ventilator gas source so that the airway pressure adheres to the setpoint. The bag/compression system in the current design may be unable to respond to changes in airway pressure with sufficient speed to implement this mode.

## 5.2 Key Safety Features

The following list provides a high-level summary of some of the most important safety requirements included in standard EN 794-3 (Lung ventilators - Part 3: Particular requirements for emergency and transport ventilators). Although it is not a complete list of all safety requirements, it is intended to highlight some of the most critical safety features to consider during design of the theoretical device. Some of these features may already be incorporated into the BVM, which can be checked by cross-referencing standard ISO 10651-4 (Lung ventilators – Part 4: Particular requirements for operator-powered resuscitators).

- During power failure, the resistance at the patient connection port to inspiratory and expiratory flows shall not exceed 0.6 kPa (6 cmH2O) at 30 l/min for adult use, 0.6 kPa at 15 l/min for paediatric use, and 0.6 kPa at 2.5 l/min for neonatal use.
- The inspiratory and expiratory resistance measured at the patient connection port shall, during spontaneous breathing and normal operation, not exceed 0.6 kPa (6 cmH2O) at 60 l/min for adult use, 30 l/min for paediatric use, and 5 l/min for neonatal use.
- The ventilator shall have a power failure alarm which activates a continuous visual signal or an auditory signal of at least 7 s duration if the internal or external, electrical or pneumatic, power supply falls below the values specified by the manufacturer.
- A high pressure alarm shall be provided. It shall activate an auditory signal when the inspiratory pressure alarm level is reached.
- The system pressure shall be limited to less than 6.6 kPa (66 cmH2O), i.e. 6.0 kPa + 10 % during normal use.
- The maximum achievable pressure at the patient connection port under single fault condition shall not exceed 10 kPa (100 cmH2O).
- Means shall be provided to prevent or indicate hypoventilation due to inadvertent reduction in inspiratory flow.
- An emergency air intake port shall be provided and shall not accept any connector complying with EN 1281-1 and EN 1281-2. The emergency air intake port should be designed so that it cannot easily be obstructed when the ventilator is in use.

# 6 Alternative Concepts

## 6.1 Anesthetic Circle System Ventilator

Inhalational volatile anesthetics are the most commonly used type of anesthetic during surgery. However, they have low solubility in the blood, so most of the anesthetic inhaled by the patient is subsequently exhaled. Anesthetic circle systems are type of ventilator system that are designed to reuse the patient’s exhaled gas to conserve anesthetic. A typical anesthetic circle system is shown in Figure 5 below.

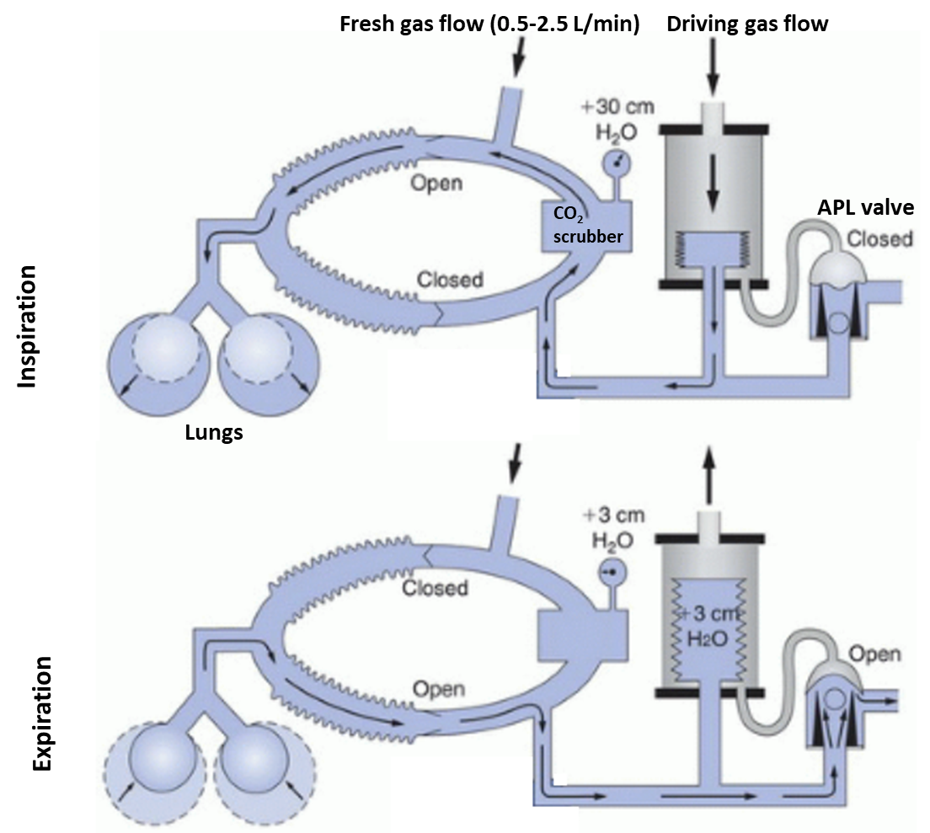
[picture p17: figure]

Figure 5: Anesthetic Circle System

During inspiration, a driving gas flow enters a rigid container with a collapsible bellows, causing the bellows to collapse and deliver gas to the patient. During exhalation, the expired has is directed back into the bellows allowing it to re-inflate.

The APL valve contains a flexible seal that, during inspiration, is forced down by the pressure of the driving gas, sealing the circuit. During expiration, the APL valve is released, allowing any expired gas in excess of the bellows volume to leave the circuit. A slight resistance in the APL valve, represented by the floating ball, ensures that during inspiration the pressure on the topside of the seal is greater than on the bottom side, causing the valve to close; during expiration, the resistance ensures that bellows fills preferentially before expired gas is released from the circuit.

The patient rebreathes previously exhaled gas which, normally, has low O2 content and high CO2 content. This is enabled by two features. Firstly, there is a CO2 scrubber in the circuit which removes CO2 from the expired gas. Secondly, a small flow of high O2 fresh gas is continuously delivered into the circuit which replenishes the oxygen supply, carries the anesthetic, and tops up any volume removed by the scrubber or lost due to leaks in the circuit.

Not shown in Figure 5 is the ventilator controller which sets the rate, flow, and pressure of the driving gas to achieve the desired ventilation profile. Title volume is usually set by either by a movable mechanical stop in the bellows container that limits the maximum height the bellows reaches on inflation or by adjusting the inspiratory time and inspiratory flow.

### 6.1.1 Relevance to the Theoretical Device

The ventilator portion of an anesthetic circle system (bellows, controller) is a fairly simple design, and available from many manufacturers in a variety of sizes with a variety of different features (Figure 6). Starting from one of these platforms may allow you to accelerate development. They often include basic rate and flow/volume controls, in addition to high and low pressure alarms. There are also companies that offer OEM versions of such ventilators¹¹ that would provide a very good base to begin development.

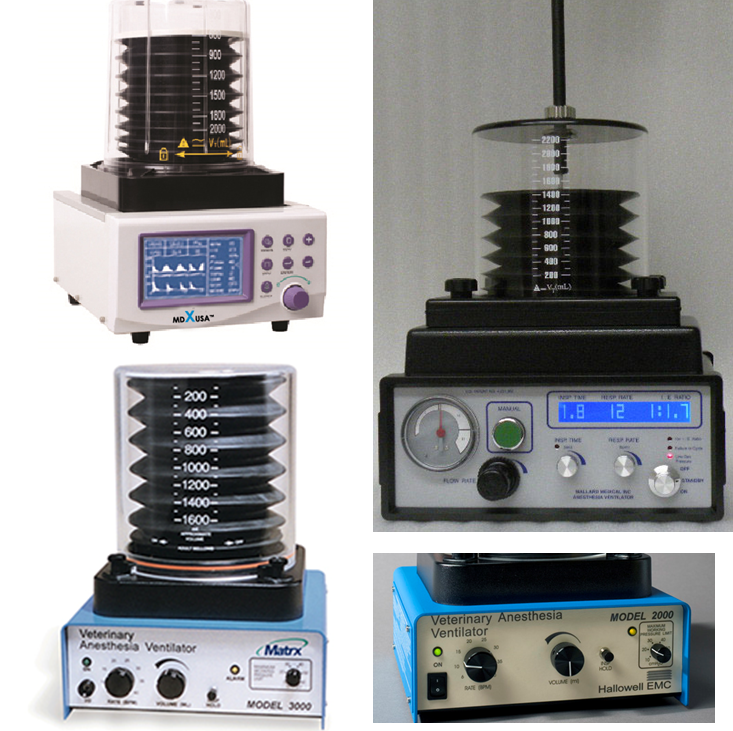
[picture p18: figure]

Figure 6: Various bellows ventilators

### 6.1.2 Challenges and Potential Solutions

The primary challenge with modifying a circle system ventilator is reinflation of the bellows. In the typical use scenario, this is accomplished by the patient’s expired gas with the appropriate scrubbers and fresh gas flows to allow for rebreathing. Without these elements, using a traditional circle system is not feasible. A potential modification to the standard circle system ventilator setup to overcome this challenge is shown in Figure 7 below.

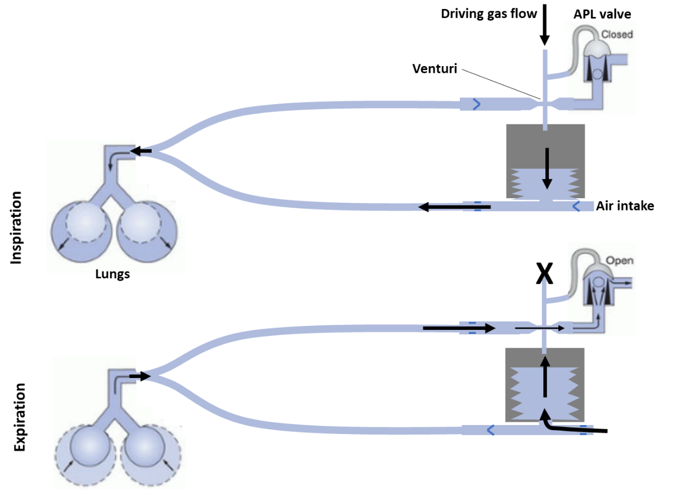
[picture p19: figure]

Figure 7: Modified circle system for bellows reinflation

In this configuration, during inspiration, the flow patterns are the same as the standard configuration – a driving gas compresses the bellows which delivers gas to the patient. During expiration, the driving gas is shut off, the APL valve opens, and the patient exhales out the APL valve through a Venturi tube. As gas passes through the narrow throat section of the Venturi, its velocity increases and, based on conservation of energy, its static pressure decreases. A venturi can be designed so that as gas passes through the throat, the pressure within the throat decreases below the ambient barometric pressure. This forms the basis of the well-known Venturi pump. By connecting the throat section of the Venturi to the bellows container, the patient’s exhaled gas may generate suction which causes the bellows to rise and draw in ambient air for the next inspiratory cycle.
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

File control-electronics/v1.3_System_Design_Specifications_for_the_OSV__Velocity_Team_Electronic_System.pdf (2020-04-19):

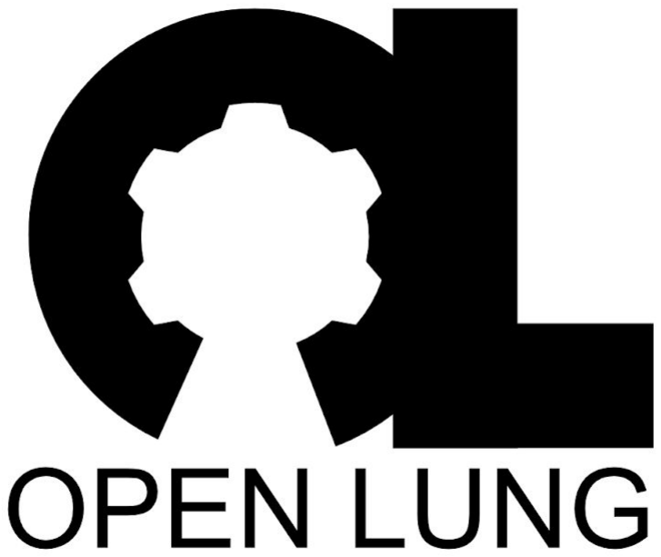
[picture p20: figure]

# System Design Specification

# Open Source Ventilator Electronic System

# Velocity Team

## Nadim Conti

Electronics System Design & coordination on behalf of the Open Source Ventilator - Open Lung Velocity team

GitLab - @nadimconti
Email - osv@nadimconti.com

Created: 30 March 2020
Last update: 19 April 2020 Version 1.3

TO DO

insert pressure sensor calculations | 6
System Introduction | 9
Links and further information | 9
Block diagram | 10
Control Loop | 12
Motor Control Loop Guideline and Overview | 12
Physiological Control Loop Guideline and Overview | 13
General Electronics requirements | 14
Environmental requirements | 14
Cost | 14
Boards size and integration | 14
PCB Layout Directives | 15
PCB Manufacturing Directives | 15
PCB Assembly Directives | 16
Schematic Design Directives | 16
Specific Electronics requirements | 18
Power Supply Unit | 18
Compatible Power Supplies: | 19
Backup Battery Pack Unit | 20
Power Supply Board | 21
Power Supply Board Dimensions and Pinout | 22
Power Supply Connectors on PSB/Motherboard | 23
Input Protection | 25
Power Management Unit | 27
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

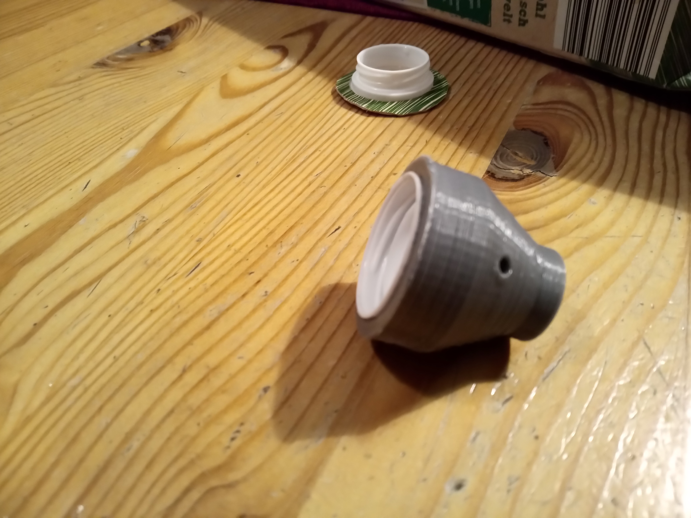
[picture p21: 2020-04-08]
mechanical-concepts/ventilator-concept-16/C16A1 (TH1)/images/C16A1_IMG_20200401_211914_8.jpg

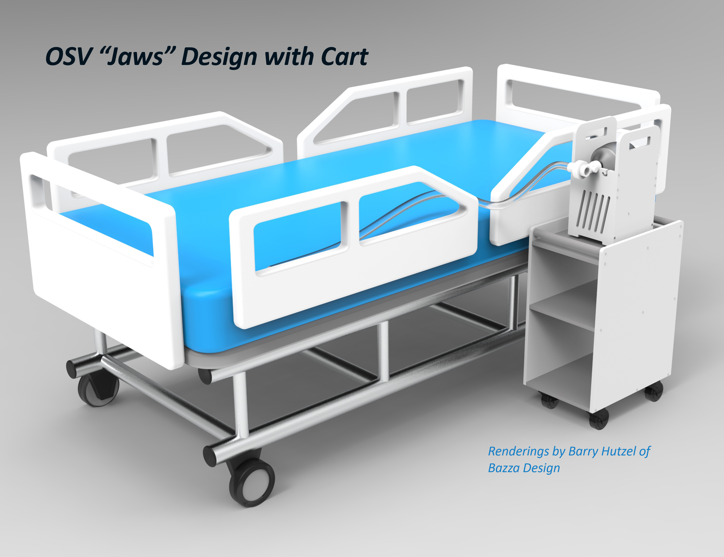
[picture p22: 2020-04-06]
mechanical-concepts/ventilator-concept-13/C13A1 (Jaws)/images/OSV side 3_4 view overall.jpg

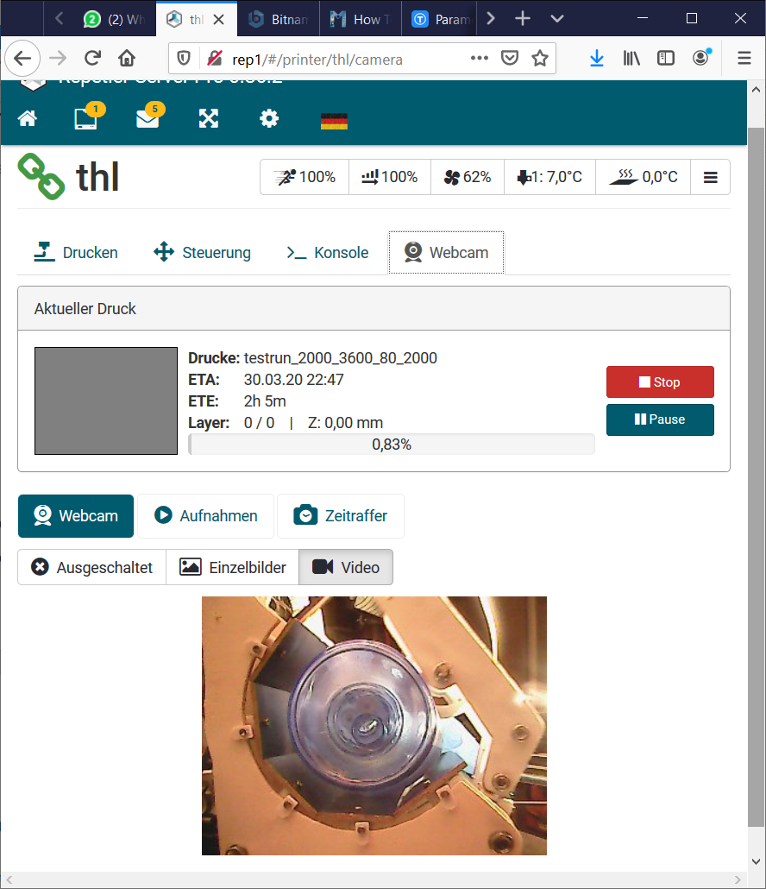
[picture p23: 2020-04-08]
mechanical-concepts/ventilator-concept-16/C16A1 (TH1)/images/C16A1_rpserv1.png

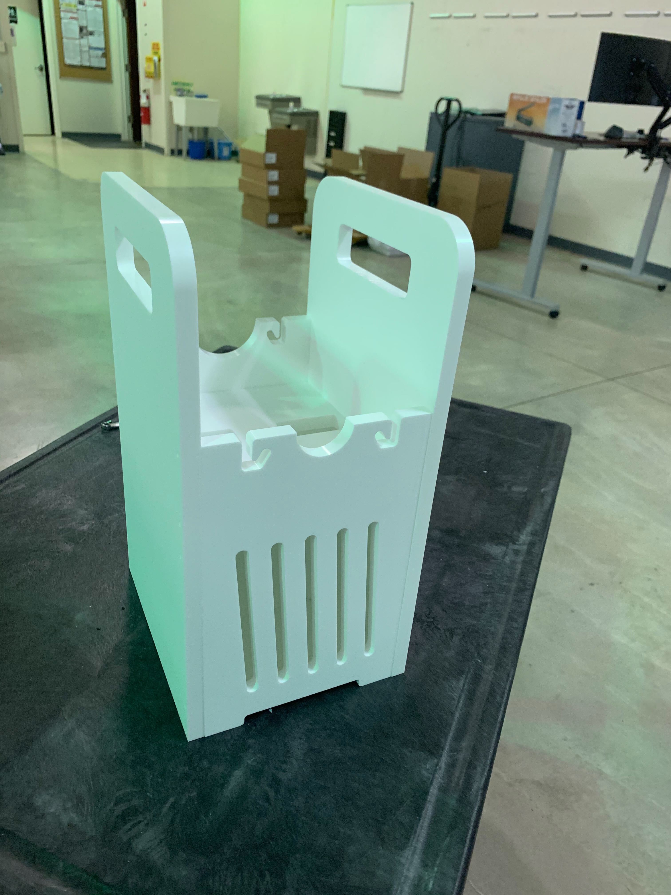
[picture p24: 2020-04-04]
mechanical-concepts/ventilator-concept-13/C13A1 (Jaws)/images/EnclosureChassis.jpg

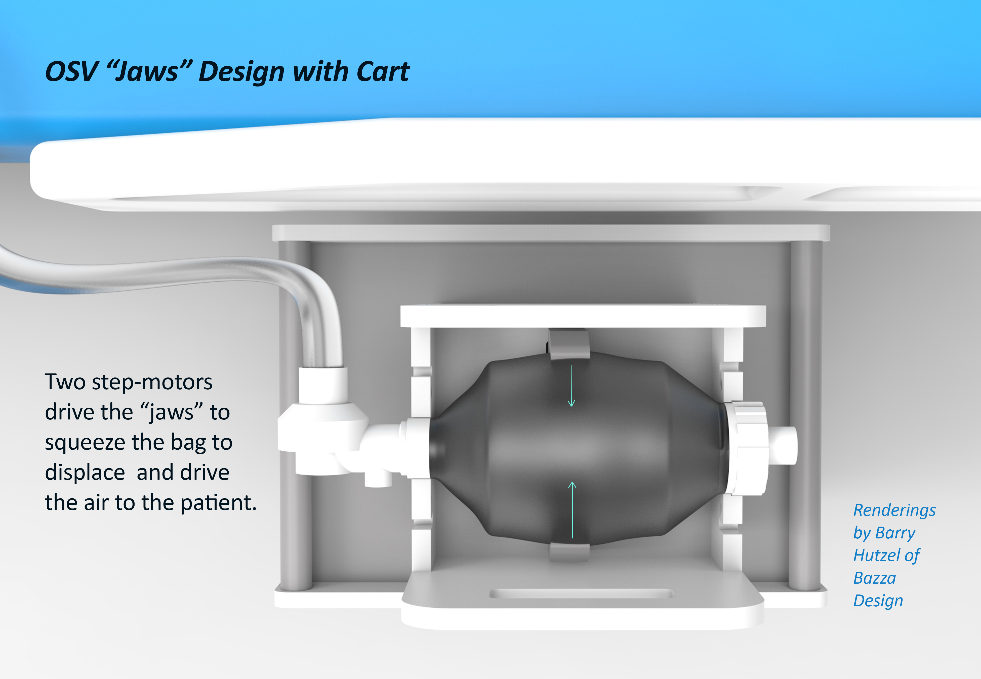
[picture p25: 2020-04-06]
mechanical-concepts/ventilator-concept-13/C13A1 (Jaws)/images/OSV top view.jpg

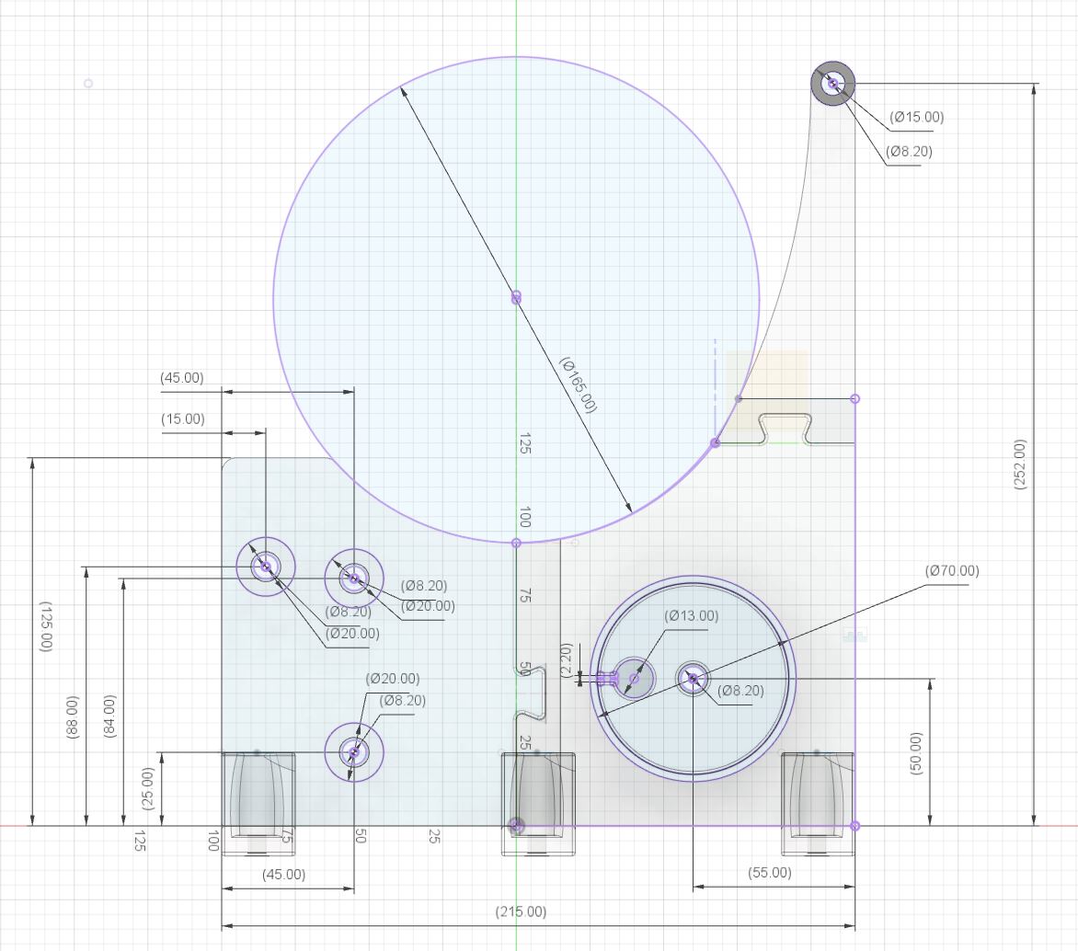
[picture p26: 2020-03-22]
mechanical-concepts/ventilator-concept-7/C7A1/images/Picture_2.JPG

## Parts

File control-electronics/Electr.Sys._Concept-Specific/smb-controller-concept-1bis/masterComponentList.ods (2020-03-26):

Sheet: microcontrollers
Name | Description | Spec Link | Suppliers
 |  |  | Supplier | Cost ea (USD)
Arduino Nano | Arduino Nano (clone) | https://store.arduino.cc/usa/arduino-nano | https://www.aliexpress.com/item/32858764759.html | 2.83
 |  |  | https://www.ebay.com/itm/Nano-V3-0-Mini-USB-ATmega328-5V-16M-Micro-controller-CH340G-board-For-Arduino-1/372857328936 | 1.93
 |  |  | https://www.amazon.com/FTCBlock-Arduino-ATmega328P-Microcontroller-Compatible/dp/B07HF5RMHV | 3.39
Arduino Pro Mini 328 | pro mini (clone) | https://store.arduino.cc/usa/arduino-pro-mini | https://www.aliexpress.com/item/710625920.html?src=google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 | 2.48
 |  |  | https://www.ebay.com/itm/New-Pro-Mini-Atmega328-5V-16M-Micro-controller-Board-Compatible-Nano-BBC/143559869934 | 1.06
 |  |  | https://www.amazon.com/flashtree-Atmega328-Development-Compatible-Arduino/dp/B07THJZJBC?rnid=2470954011&rps=1 | 4.99

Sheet: sensors
Name | Description | Spec Link | Suppliers
 |  |  | Supplier | Cost (USD)
BME280 | Pressure/Temperature/Humidity/Barometric digital sensor | https://www.bosch-sensortec.com/media/boschsensortec/downloads/datasheets/bst-bme280-ds002.pdf | https://www.aliexpress.com/item/32863566266.html | 3.4
 |  |  | https://www.ebay.com/itm/BME280-Atmospheric-Pressure-Sensor-Temperature-Humidity-Sensor-For-Arduino-New/274013225432 | 0.86
MPX53DP | Pressure sensor | https://www.nxp.com/docs/en/data-sheet/MPX53.pdf | https://www.digikey.com/product-detail/en/nxp-usa-inc/MPX53DP/MPX53DP-ND/951812?productid=951812 | 12.74
MPS20N0040D-D | Pressure sensor | https://softroboticstoolkit.com/files/sorotoolkit/files/mps20n0040d-s_datasheet.pdf | https://www.ebay.com/itm/MPS20N0040D-D-Sphygmomanometer-Pressure-Sensor-0-40kPa-DIP-6-For-Arduino-NEW/264489544469?epid=0 | 1.86
SHT35 | Pressure/Humidity | https://media.digikey.com/pdf/Data%20Sheets/Sensirion%20PDFs/HT_DS_SHT3x_DIS.pdf | https://www.digikey.com/product-detail/en/101020592/1597-1684-ND/9697030?WT.z_cid=ref_octopart_dkc_buynow&curr=usd&site=us | 14.18
HTU31D | Pressure/Humidity | https://www.te.com/commerce/DocumentDelivery/DDEController?Action=showdoc | no direct supply, waiting on company details | ?
SM6331 | Diff pressur sensor | https://www.si-micro.com/fileadmin/00_smi_relaunch/product_tables/preliminary/SM6331-BCE-S-004-000.pdf | no direct supply, waiting on company details | ?
MPX2010 | Pressure sensor | https://4donline.ihs.com/images/VipMasterIC/IC/FSCL/FSCLS04131/FSCLS04131-1.pdf?hkey=EC6BD57738AE6E33B588C5F9AD3CEFA7 | https://www.rocelec.com/part/FREFREMPX2010GP | 9.39
2SMPP-03 | Pressure sensor | https://omronfs.omron.com/en_US/ecb/products/pdf/en-2smpp-03.pdf | https://www.digikey.com/product-detail/en/omron-electronics-inc-emc-div/2SMPP03/Z3639-ND/3671590 | 7.66

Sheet: actuators
Name | Description | Spec Link | Suppliers
 |  |  | Supplier | Cost (USD)
A4988 Stepper Motor | Stepper motor controller |  | https://www.aliexpress.com/item/1851964212.html | 4.43
SFM-27 Buzzer | SFM-27 DC 3-24V 90DB Intermittent Beep Alarm Electronic Buzzer | https://opencircuit.shop/resources/file/7379f0193d4549c771f0d61bd31d06b316cd4706466/SFM27-Datasheet.pdf | https://www.aliexpress.com/item/32671465979.html | 4.47

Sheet: hmi
Name | Description | Spec Link | Suppliers
 |  |  | Supplier | Cost (USD)
TM1638 |  |  | https://www.aliexpress.com/item/32807348409.html | 1.42
KY-040 | Rotary Encoder | http://eeshop.unl.edu/pdf/KEYES%20Rotary%20encoder%20module%20KY-040.pdf | https://www.aliexpress.com/item/32881217457.html?s=p&ad_pvid=20200325185050736469601899940004932872_1 | 0.87
TM1637 | 4-bit LED Display module | https://retrocip.cz/files/tm1638.pdf | https://www.aliexpress.com/item/1969258031.html | 0.94

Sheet: power
Name | Description | Spec Link | Suppliers
 |  |  | Supplier | Cost (USD)
DC-DC Buck Regulator | DC regulation | http://www.ti.com/lit/ds/symlink/lm2596.pdf | https://www.aliexpress.com/item/1859113573.html | 4.55

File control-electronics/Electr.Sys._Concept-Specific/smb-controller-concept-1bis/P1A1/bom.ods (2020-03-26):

Name (see masterComponentList) | Quantity
mircocontroller/Arduino Nano | 1
hmi/TM1638 | 1
sensors/BME280 | 1
power/DC-DC Buck Regulator | 1
A4988 Stepper Motor | 1
3D printed controller housing | 1
12V/?A power supply jack | 1
connector to motor?
connector to BME280?
housing for BME280?

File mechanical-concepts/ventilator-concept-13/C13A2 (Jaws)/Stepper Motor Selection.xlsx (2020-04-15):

Force Calculation
Efficiency of system | 80%
Lever Arm | 5.5 | in |  | Pitch | Input (teeth) | Input (diameter) | Output (teeth) | Output (diameter) | Reduction
Force Required | 30 | lbs | Gear Reduction #1 | 32 | 12 | 0.375 | 128 | 4 | 10.66666667
Required Torqued | 2640 | oz*in | Gear Reduction #2 | 16 | 12 | 0.75 | 72 | 4.5 | 6.00
Number of motors | 2 |  |  |  |  |  |  | Total: | 64
Gear Reduction | 64
Motor Torque required | 25.78 | oz*in | Motor Selection
RPM (selected by team) | 175 | rpm
RPM of Lever Arm | 2.734375 | rpm
Revutions required of lever, for full compression | 30 | degrees
Dwell at full compression (guess) | 0.5 | seconds
Time for complete cycle | 11.47142857 | seconds
Cycles per minute | 5.230386052

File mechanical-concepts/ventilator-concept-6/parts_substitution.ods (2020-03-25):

orig_part | sub_part | sub_stl_url | avail_europe | avail_northAmerica | avail_southAmerica | avail_africa | avail_asia | comment
Spacer | Sched 40 PVC pipe |  |  | X |  |  |  | would require modification to plate and possibly a new, smaller, component to integrate the pipe. Models in work.

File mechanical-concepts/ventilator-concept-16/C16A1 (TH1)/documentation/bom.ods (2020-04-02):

Part Number | Quantity | Part Cost ea (USD) | Description | Manufacturer | Total Cost
 |  |  |  |  | $0.00

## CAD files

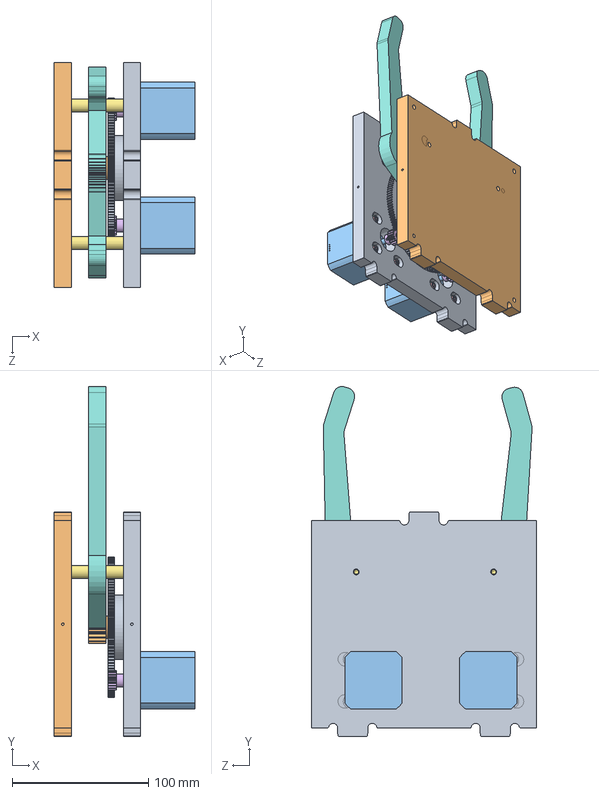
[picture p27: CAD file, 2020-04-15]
mechanical-concepts/ventilator-concept-13/C13A1 (Jaws)/models/OSV Velocity - Jaws concept/r_000_4_1_2020/R_200_ASM.sldasm
103.4 x 257.2 x 165.1 mm
R_200_01
STP-MTR-17040 x 2
91116A120_TYPE_18-8_STAINLESS_S x 8
91292A029_TYPE_18-8_SS_SOCKET_H x 8
RUSHGEARS__1135-5925 x 2
R_200_03 x 2
R_203_01 x 2
RushGears__TA32128A
RushGears_2017_YA2017

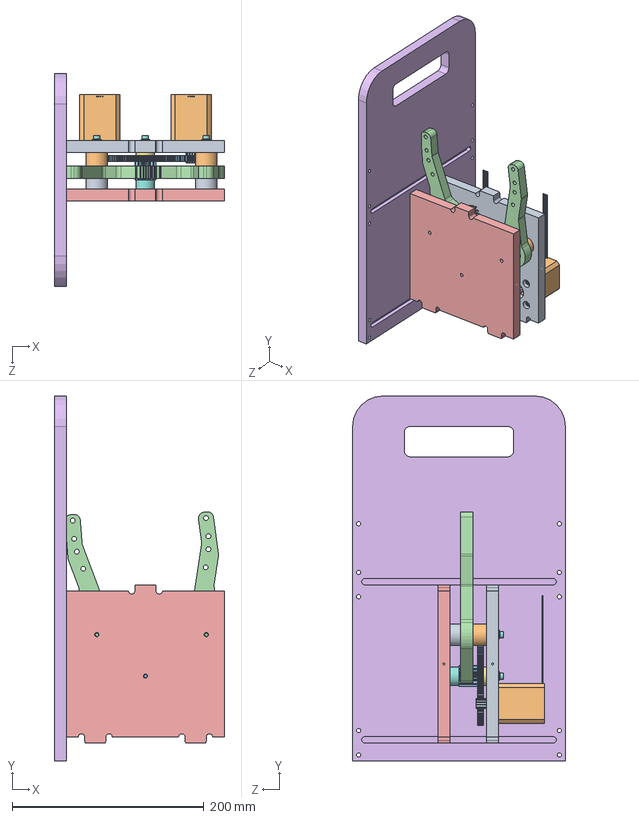
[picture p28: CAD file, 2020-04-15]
mechanical-concepts/ventilator-concept-13/C13A2 (Jaws)/Ventilator_R_001_2020-04-01/R_ASSY_200.SLDASM
177.5 x 381.0 x 222.2 mm
R_200_01_rev2
STP-MTR-17048 x 2
R_200_03_rev2
R_200_04 x 2
91116A120_TYPE 18-8 STAINLESS STL OVERSIZED FLAT WASHER x 8
91292A027_TYPE 18-8 SS SOCKET HEAD CAP SCREW x 8
92141A009_TYPE 18-8 STAINLESS STEEL FLAT WASHER x 3
92196A198_18-8 STAINLESS STEEL SOCKET HEAD CAP SCREW x 3
12t_Steel_Spur_Gear_32_DP_RS775_Motor_217-5859.step x 2
6391K127_OIL-EMBEDDED SLEEVE BEARING x 2
R_200_05
R_203_01_rev2 x 2
R_200_02_rev2
R_200_06_SPCR
R_200_07_SPCR
R_200_08_SPCR x 2
R_200_09_SPCR x 2

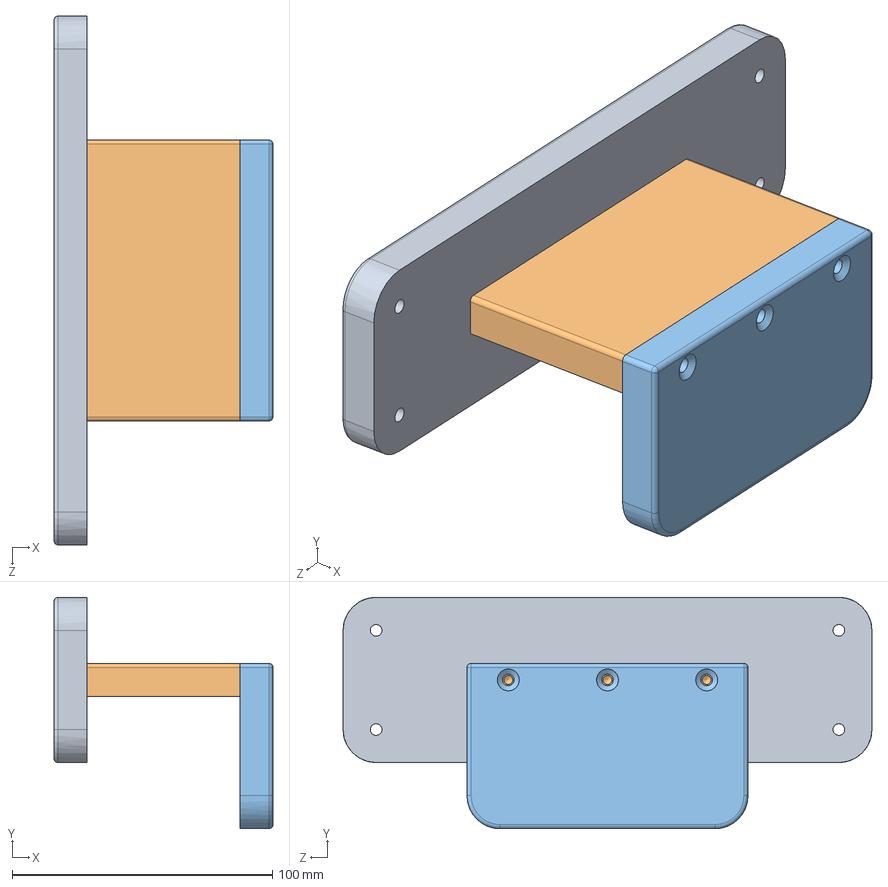
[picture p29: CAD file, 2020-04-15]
mechanical-concepts/ventilator-concept-13/C13A2 (Jaws)/Ventilator_R_002_2020-04-06/Archieve (Development)/R_ASSY_300_Rev3.SLDASM
84.1 x 88.9 x 203.2 mm
R_300_03_rev3
R_300_01_rev3
R_300_02_rev3

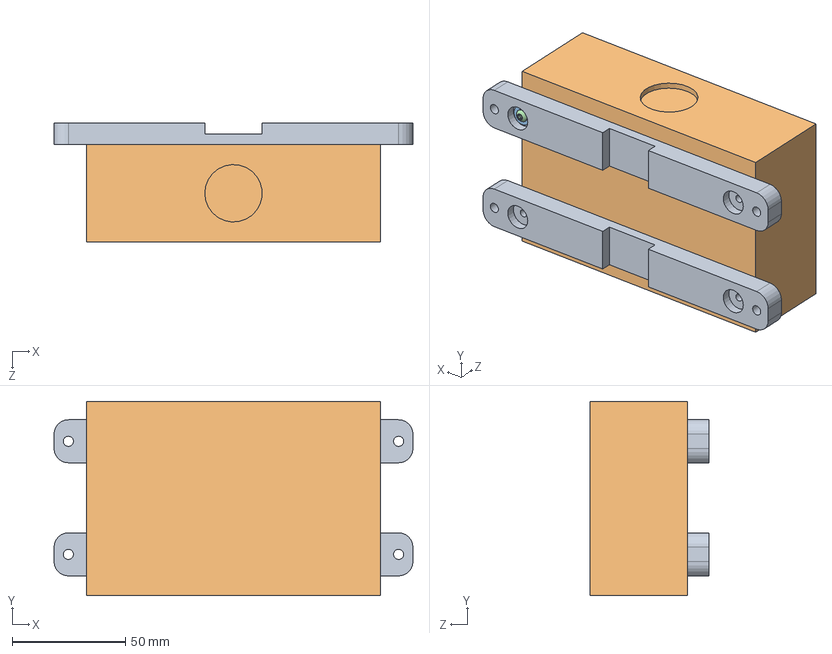
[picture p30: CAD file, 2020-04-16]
mechanical-concepts/ventilator-concept-13/C13A2 (Jaws)/Ventilator_R_002_2020-04-06/R_ASSY_300.SLDASM
158.8 x 86.0 x 52.5 mm
R_300_01 x 2
RPS-400-48-C
91116A120_TYPE 18-8 STAINLESS STL OVERSIZED FLAT WASHER
92095A181_BUTTON HEAD HEX DRIVE SCREW

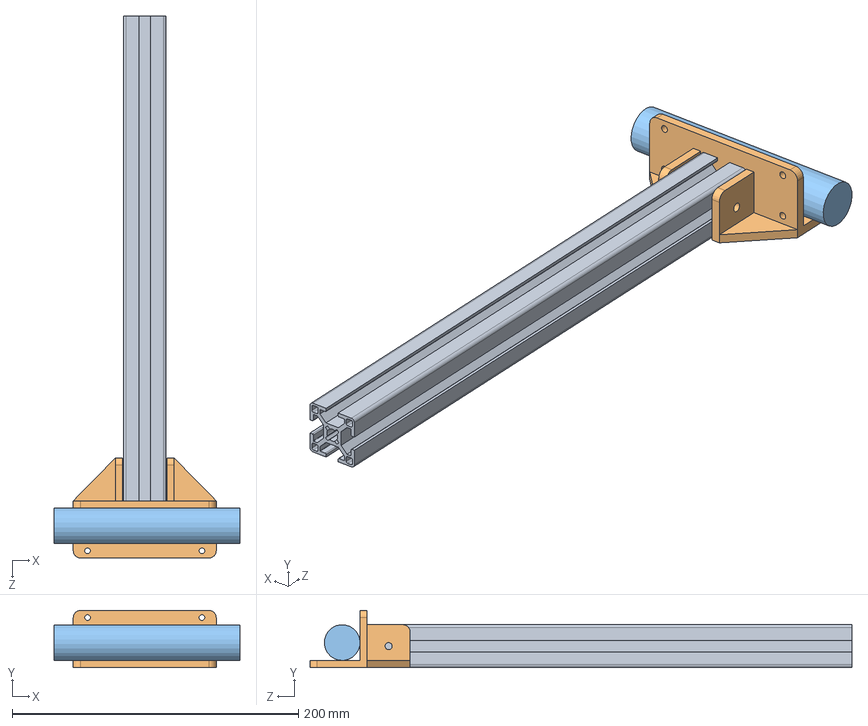
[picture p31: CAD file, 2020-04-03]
mechanical-concepts/ventilator-concept-15/C15A1/CXI-A-0003.SLDASM
130.0 x 40.0 x 379.0 mm
CXI-P-0001
CXI-P-0011
CXI-P-0012

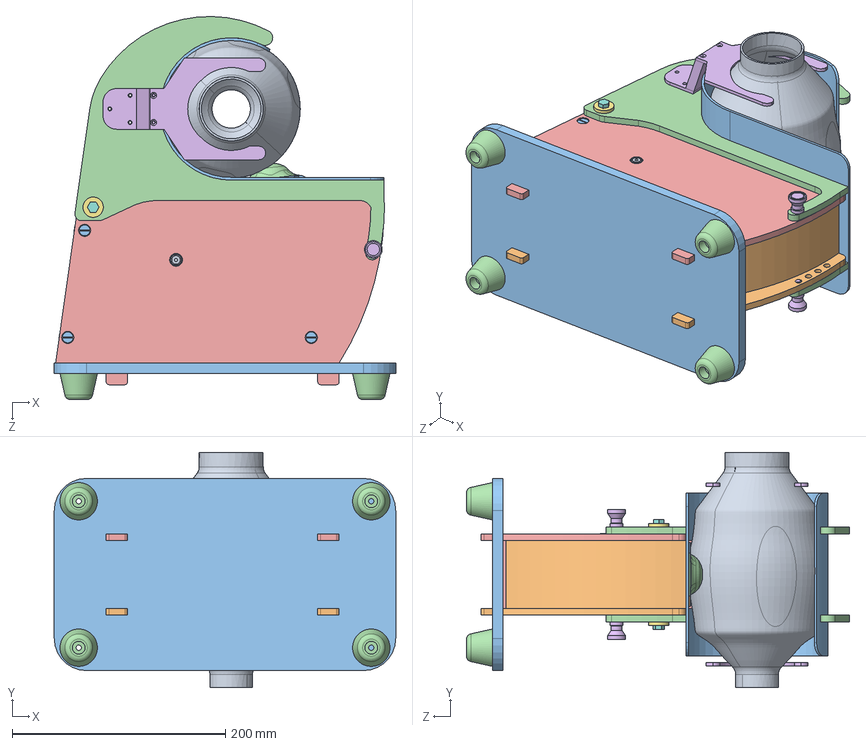
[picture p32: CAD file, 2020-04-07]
mechanical-concepts/ventilator-concept-8/C8B2 (Maker)/C8B2 Assembly/Assem - David Concept 8.2.SLDASM
320.0 x 220.2 x 358.9 mm
BVM - pressure bag
Rib AA.12
bed B
Rib AA.11 x 2
back cover B
INDEXING PLUNGER x 2
collar A x 2
Bolt - Pivot 0.25DIA. x 2
screw .125DIA. x 4
front cover C
screw .25DIA. x 8
spacer machined bar A x 4
Rib AA.9
LATERAL BRACE A x 2
WASHER, .25 ID, .625 OD
BOLT, 12-28, .375L
COBDesign -Flapper FRONT -030
COBDesign -Flapper LHS -028
COBDesign -Flapper RHS -027
COBDesign -Flapper TOP -029
igus_69-20122019-062104_33cdeqpqasiwtsivn7gctalp9 x 6
COBDesign -Igus Nut Mount -024
igus_wfrm-252525tr10x2_Igus Nut For Prototype
ROCKCLIFF-CNC-NEMA23-STEPPER-MOTOR
COBDesign -NEMA 23 Mount -031
COBDesign -Igus Lead Screw -034
Part13^Assem - David Concept 8.2
COBDesign -Foot PAD -036 x 4

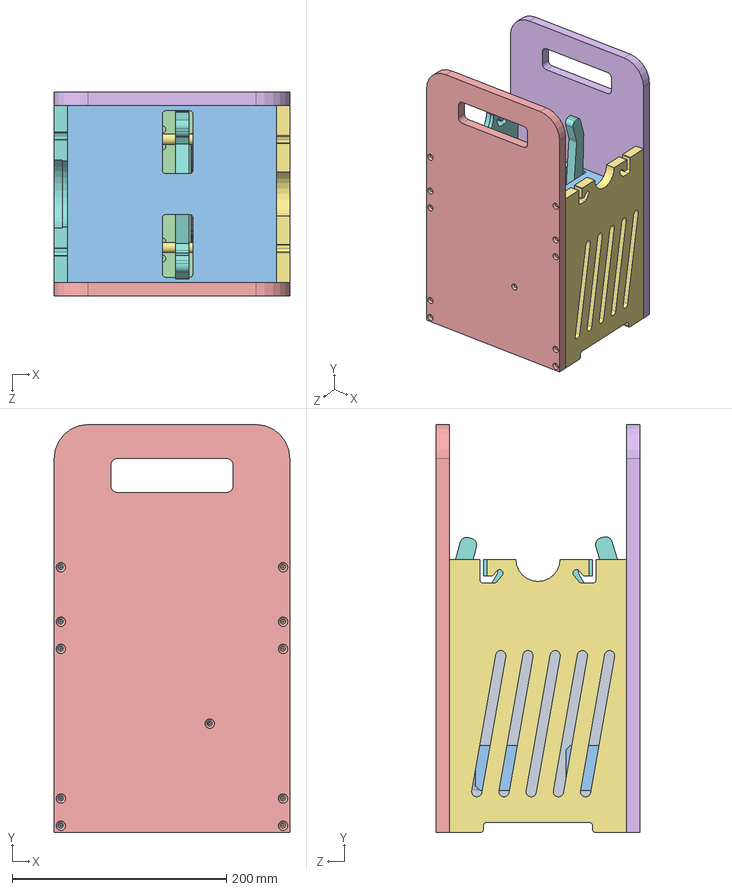
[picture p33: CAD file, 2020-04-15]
mechanical-concepts/ventilator-concept-13/C13A1 (Jaws)/models/OSV Velocity - Jaws concept/r_000_4_1_2020/r_000_4_1_2020.sldasm
220.1 x 381.0 x 190.5 mm
R_200_01
R_200_02
STP-MTR-17040 x 2
91116A120_TYPE_18-8_STAINLESS_S x 8
91292A029_TYPE_18-8_SS_SOCKET_H x 8
RUSHGEARS__1135-5925 x 2
R_200_03 x 2
R_203_01 x 2
RushGears__TA32128A
RushGears_2017_YA2017
R_100_01
R_100_02
R_100_03
R_100_04
R_100_05
R_100_06

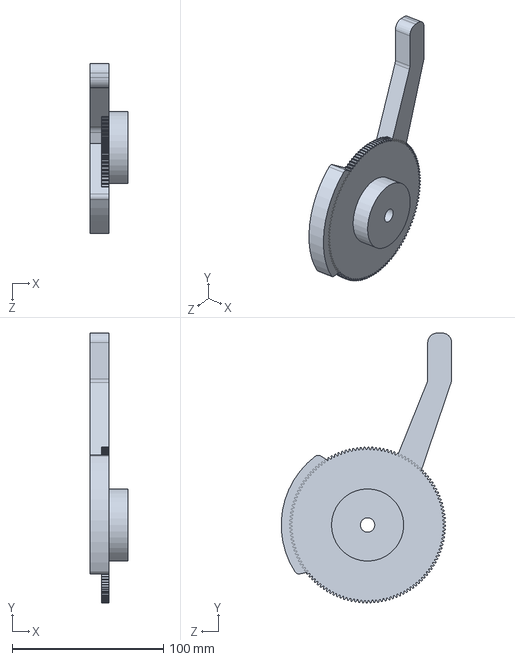
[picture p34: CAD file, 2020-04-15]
mechanical-concepts/ventilator-concept-13/C13A2 (Jaws)/Backup Copies/r_000_4_1_2020/R_203_ASM.sldasm
25.4 x 178.6 x 112.7 mm

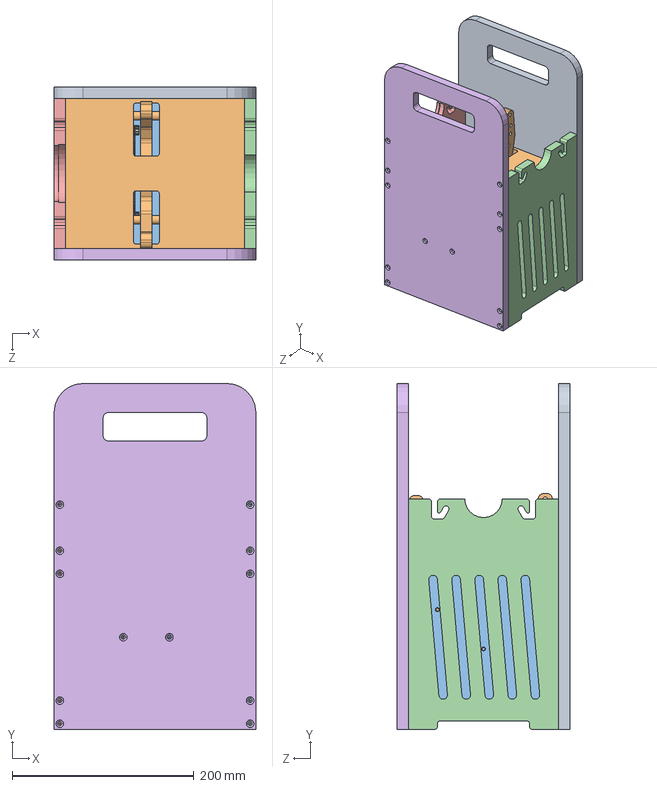
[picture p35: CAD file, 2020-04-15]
mechanical-concepts/ventilator-concept-13/C13A2 (Jaws)/Ventilator_R_001_2020-04-01/R_ASSY_000_rev2.SLDASM
222.2 x 381.0 x 190.5 mm
R_100_04_rev2
R_100_01_rev2
R_100_02_rev2
R_100_05 rev2
R_100_06 rev2
R_100_03_rev2
R_200_01_rev2
STP-MTR-17048 x 2
R_200_03_rev2
R_200_04 x 2
91116A120_TYPE 18-8 STAINLESS STL OVERSIZED FLAT WASHER x 8
91292A027_TYPE 18-8 SS SOCKET HEAD CAP SCREW x 8
92141A009_TYPE 18-8 STAINLESS STEEL FLAT WASHER x 3
92196A198_18-8 STAINLESS STEEL SOCKET HEAD CAP SCREW x 3
12t_Steel_Spur_Gear_32_DP_RS775_Motor_217-5859.step x 2
6391K127_OIL-EMBEDDED SLEEVE BEARING x 2
R_200_05
R_203_01_rev2 x 2
R_200_02_rev2

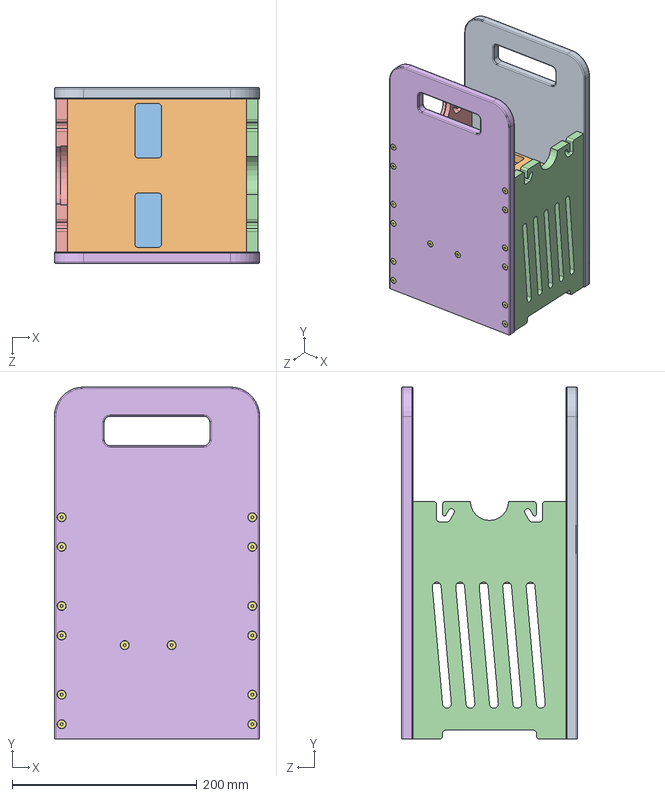
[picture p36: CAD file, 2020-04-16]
mechanical-concepts/ventilator-concept-13/C13A2 (Jaws)/Ventilator_R_002_2020-04-06/R_ASSY_100_Rev3.SLDASM
222.2 x 381.0 x 190.5 mm
R_100_04_rev3
R_100_01_rev3
R_100_02_rev3
R_100_05 rev3
R_100_06 rev3
R_100_03_rev3
95893A950_THREAD-FORMING TORX SCREW FOR PLASTICS x 28

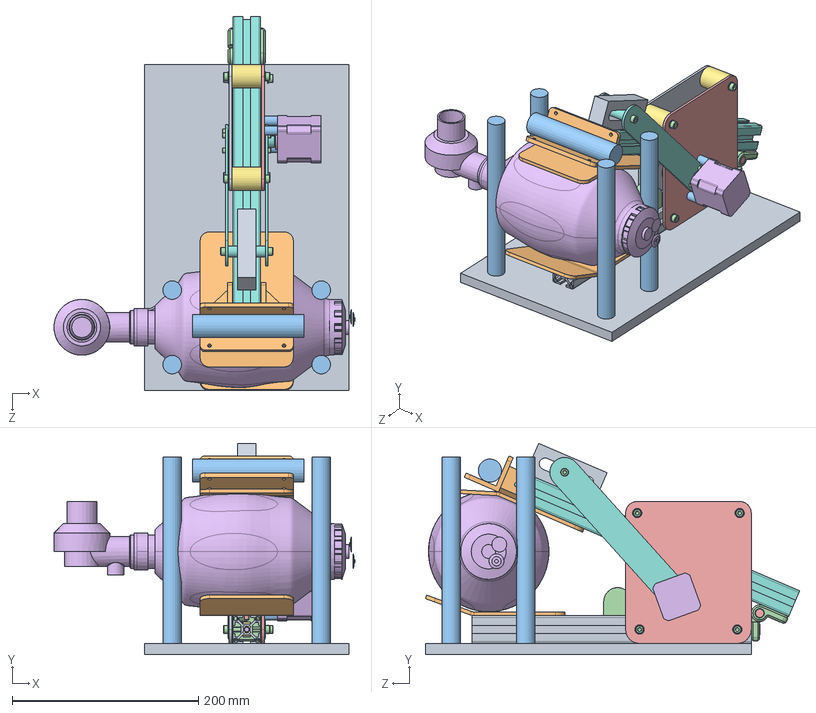
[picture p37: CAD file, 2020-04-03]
mechanical-concepts/ventilator-concept-15/C15A1/CXI v2.SLDASM
323.2 x 226.9 x 401.9 mm
CXI-P0001
CXI-P-0003 x 2
CXI-P-0010 x 4
Rexroth-3 842 535 687_Style 2 x 2
Rexroth-3 842 535 687_Pin-2
Rexroth-3 842 535 687_Screw x 2
Rexroth-3 842 535 687_30Series x 2
CXI-P-0001
CXI-P-0004
CXI-P-0011
CXI-P-0012
CXI-P-0009
CXI-P-0005
NEMA 17 Stepper Motor
CXI-P-0006 x 2
CXI-P-0007
CXI-P-0013
plain washer grade a_din x 12
CXI-P-0008 x 3
socket head cap screw_din x 22
socket countersunk head screw_din x 4
BVM_montado

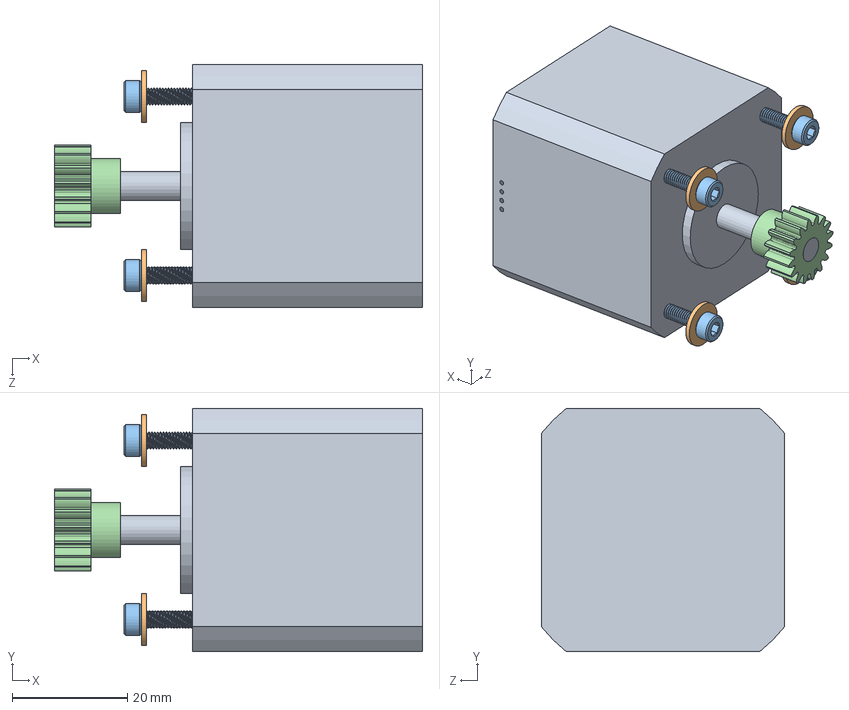
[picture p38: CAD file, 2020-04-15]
mechanical-concepts/ventilator-concept-13/C13A2 (Jaws)/Backup Copies/r_000_4_1_2020/R_201_ASM.sldasm
63.8 x 42.2 x 42.2 mm
STP-MTR-17040
91116A120_TYPE_18-8_STAINLESS_S x 4
91292A029_TYPE_18-8_SS_SOCKET_H x 4
RUSHGEARS__1135-5925

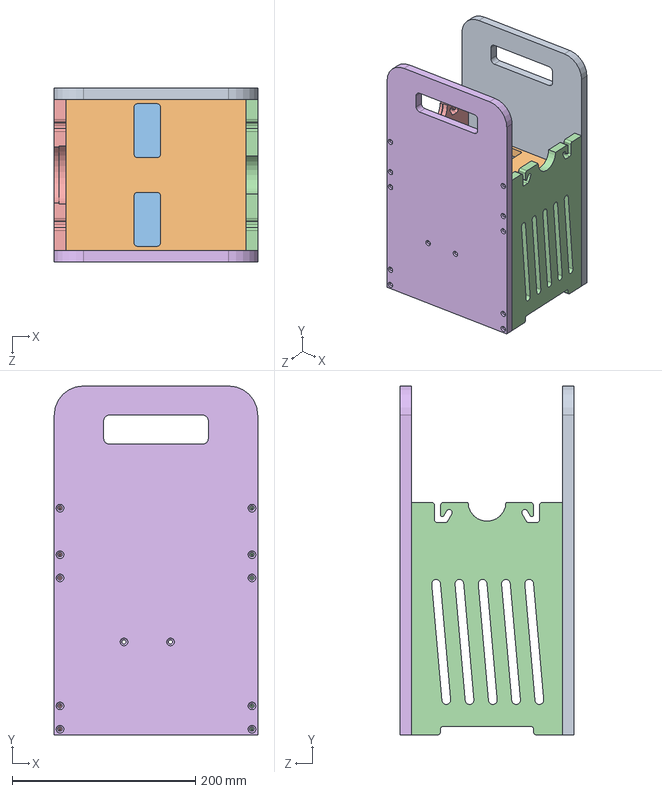
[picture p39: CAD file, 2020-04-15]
mechanical-concepts/ventilator-concept-13/C13A2 (Jaws)/Ventilator_R_001_2020-04-01/R_ASSY_100.SLDASM
222.2 x 381.0 x 190.5 mm
R_100_04_rev2
R_100_01_rev2
R_100_02_rev2
R_100_05 rev2
R_100_06 rev2
R_100_03_rev2

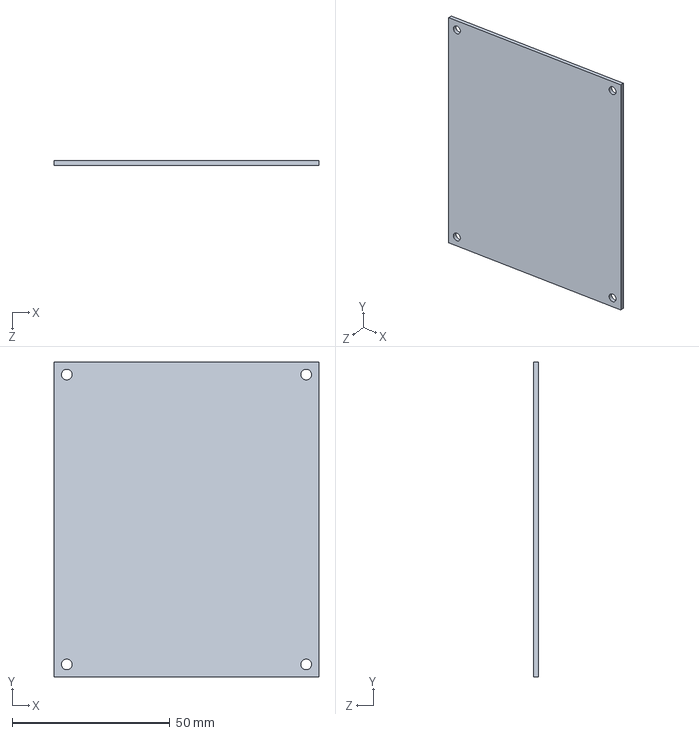
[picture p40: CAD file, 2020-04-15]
mechanical-concepts/ventilator-concept-13/C13A2 (Jaws)/Ventilator_R_002_2020-04-06/Main Elec Board Place Holder.SLDPRT
84.0 x 100.0 x 1.59 mm

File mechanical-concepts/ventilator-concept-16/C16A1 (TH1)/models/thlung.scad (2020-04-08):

pads=0;

plastik="red";
alu    ="white";
steel    ="darkgrey";
filament    ="red";

nema17=31/2;
moth=40;
plateth=3;
axdist=100;
axdia=8;
rbig=40;

b608dia=22;
b608h=7;


lagerod=b608dia;
lagerh=8;
actorh=lagerh;
actord=80;
armrot=45;
frameih=30;

roddia=8;
lagerdia=22;
roddistx=lagerdia*2;
bagdia=165;
bagl=165;
bagl2=165+150;
outletdia=80;
beltwidth=20;
plate1w=bagdia+20;
plate1l1=0;
plate1l2=175;
stampdia=100;
stampfixdist=80;
myx=(bagdia/3+plate1w*1.4)/2;
    echo(str("myx=",myx));

    segoff=8;
ml=230;//350;
mindist=60;//belt 16 (2 bearings), washer 4*1
pusherlen=60;
angle=10;
stamprot=10;
bagz=150;

angle=20-$t*30;

actorw=60;
//projection(cut=false){actor2a();}
main2();
//actor1(1);
//pad(22);
//actor1(0);

//boardclip();

//motholder();



//translate([0,0,bagz])rotate([90,0,0])%hull()bag();
//translate([0,40+10,0])rotate([90,0,0])motor();
//translate([0,0,bagz])rotate([90,0,0])arm();
//roller(70,40-4);

module roller(d,b){
    th=3;
    rand=10;
    difference(){
        union(){
            difference(){
               sphere(d=d,$fn=64);
               mirror([0,0,1])cylinder(r=d,h=d); 
               translate([0,0,b/2])cylinder(r=d,h=d); 
               translate([0,0,-1])cylinder(d=d-rand*2,h=d,$fn=256); 
            }
            for(i=[0,120,240])
                 rotate([0,0,i])hull(){
                 translate([d/2-rand,0,0])cylinder(d=10,h=b/2);
                 translate([0,0,0])cylinder(d=10,h=b/2);
                 }
            cylinder(d=b608dia+2*th,h=b/2,$fn=64);
            
            }
        translate([0,0,b/2-b608h])
            cylinder(d=b608dia+.7,h=b/2,$fn=64);
        translate([0,0,b/2-b608h-2])
            cylinder(d=b608dia-3,h=b/2,$fn=64);
        translate([0,0,-1])
            cylinder(d=b608dia-3,h=b/2,$fn=64);
        for(i=[0,120,240])
            rotate([0,0,i])
             translate([d/2-rand,0,-1])cylinder(d=2.5,h=b/2+2);
    }
}


module motholder(){

th=plateth;
th2=8;
    motoff=10;
    fixlen=30;
    fixw=30;
    if(pads>0){
        translate([-60,0,0])pad(22);
        translate([0,25,0])pad(22);
        translate([0,-25,0])pad(22);
        translate([70,15,0])pad(22);
        translate([70,-15,0])pad(22);
        }
    
    difference(){
        union(){
            hull(){
                translate([-roddistx,0,0])cylinder(d=roddia*3,h=th);
                translate([0,0,0])cylinder(d=roddia*3,h=th);
                translate([nema17*2+motoff,-fixw/2,0])
                    cylinder(d=8,h=th);
                translate([nema17*2+motoff, fixw/2,0])
                    cylinder(d=8,h=th);
                translate([nema17*2+motoff+fixlen,-fixw/2,0])
                    cylinder(d=8,h=th);
                translate([nema17*2+motoff+fixlen, fixw/2,0])
                    cylinder(d=8,h=th);            }
            translate([0,0,0])
            rotate([0,0,45])
            hull()
            for(a=[0,90,180,270]){
                rotate([0,0,a])
                translate([-16,-16,0])
                  cylinder(d=8,h=plateth, $fn=32);
            }
                translate([0,0,0])cylinder(d=nema17*3,h=th);
            hull(){
                translate([nema17*2+motoff+fixlen,-fixw/2,0])
                    cylinder(d=8,h=th2);
                translate([nema17*2+motoff,fixw/2,0])
                    cylinder(d=8,h=th2);
            }
            hull(){
                translate([nema17*2+motoff,-fixw/2,0])
                    cylinder(d=8,h=th2);
                translate([nema17*2+motoff+fixlen, fixw/2,0])
                    cylinder(d=8,h=th2);
            }
        }
        translate([-roddistx,0,-1])cylinder(d=roddia+1,h=th+2);
        hull(){
        translate([-roddistx,0,-1])cylinder(d=roddia,h=th+2);
        translate([-roddistx-50,0,-1])cylinder(d=roddia,h=th+2);
        }
        translate([0,0,-1])cylinder(d=5,h=th+2);
            translate([0,0,0])
            rotate([0,0,45])
            for(a=[0,90,180,270]){
                rotate([0,0,a])
                translate([-16,-16,-1])
                  cylinder(d=3,h=th+2, $fn=32);
                
            }
            translate([0,0,-1])
                cylinder(d=24,h=th+2);
            translate([plate1w,0,-1])cylinder(d=roddia,h=th+2);
                translate([nema17*2+motoff,-fixw/2,-1])
                    cylinder(d=2.5,h=th2+2);
                translate([nema17*2+motoff, fixw/2,-1])
                    cylinder(d=2.5,h=th2+2);
                translate([nema17*2+motoff+fixlen,-fixw/2,-1])
                    cylinder(d=2.5,h=th2+2);
                translate([nema17*2+motoff+fixlen, fixw/2,-1])
                    cylinder(d=2.5,h=th2+2);
    }
}


module boardclip(){
   difference(){
       union(){
           translate([0,0,plateth])
                cube([8,8,2*plateth],center=true);
           cylinder(d=8,h=2*plateth,$fn=32);
           hull(){
           cylinder(d=8,h=plateth,$fn=32);
           translate([6,0,0])
           cylinder(d=8,h=plateth,$fn=32);
           }
       }
    translate([0,0,-1])cylinder(d=3.5,h=2*plateth+2,$fn=32);
    translate([3,0,2*plateth])
        cube([8,10,2*plateth],center=true);
       
   } 
}
module pad(d){
    cylinder(d=d,h=.5,$fn=64);
    
    }
module actor1(lager){
    th=plateth;
    actw=actorw;
    disty=50-10;
    dyoff=10+2;
    myd=8;
    if (pads>0){
              if(lager>0){  
    translate([-actw/2,20,0])pad(22);
    translate([ actw/2,20,0])pad(22);
              }
    translate([-actw/2,-20,0])pad(22);
    translate([ actw/2,-20,0])pad(22);
    translate([-actw/2,-80,0])pad(22);
    translate([ actw/2,-80,0])pad(22);
          }
    difference(){
        union(){
            
            if(lager>0){
                translate([-actw/2,0,th+b608dia/2])actor0();
                translate([ actw/2,0,th+b608dia/2])actor0();

                hull(){
                translate([-(actw-5)/2,-(b608dia/2+4),0])
                    cylinder(d=5,h=b608dia/2,$fn=32,
                                            center=false);
                translate([ (actw-5)/2,-(b608dia/2+4),0])
                    cylinder(d=5,h=b608dia/2,$fn=32,
                                            center=false);
                translate([-(actw-5)/2,-(b608dia/2+4)-dyoff,0])
                    cylinder(d=5,h=b608dia/2,$fn=32,
                                            center=false);
                translate([ (actw-5)/2,-(b608dia/2+4)-dyoff,0])
                    cylinder(d=5,h=b608dia/2,$fn=32,
                                            center=false);
                }
            }
            
            
            
            hull(){
    translate([ 0,-(b608dia/2+4)-5-dyoff-disty/2,0]){
        translate([-(actw-myd)/2, (disty/2+myd),0])
        cylinder(d=myd,h=b608dia/2,$fn=128,center=false);  
        translate([ (actw-myd)/2, (disty/2+myd),0])
        cylinder(d=myd,h=b608dia/2,$fn=128,center=false);  
    }

            translate([-(actw-myd)/2,-(b608dia/2+4)-dyoff,0])
                cylinder(d=myd,h=b608dia/2,$fn=32,
                                        center=false);
            translate([ (actw-myd)/2,-(b608dia/2+4)-dyoff,0])
                cylinder(d=myd,h=b608dia/2,$fn=32,
                                        center=false);
            translate([-(actw-myd)/2,-(b608dia/2+4)-dyoff*2-disty,0])
                cylinder(d=myd,h=b608dia/2,$fn=32,
                                        center=false);
            translate([ (actw-myd)/2,-(b608dia/2+4)-dyoff*2-disty,0])
                cylinder(d=myd,h=b608dia/2,$fn=32,
                                        center=false);
            }          


        }
    translate([-actw/2,-(b608dia/2+4),-1])
        cylinder(d=2.5,h=b608dia/2+2,$fn=32,center=false);
    translate([ actw/2,-(b608dia/2+4),-1])
        cylinder(d=2.5,h=b608dia/2+2,$fn=32,center=false);
    translate([ 0,-(b608dia/2+4)-5-dyoff-disty/2,b608dia/4])
        cylinder(d=disty,h=b608dia,$fn=128,center=true);
        
    translate([ 0,-(b608dia/2+4)-5-disty/2-dyoff+disty/2,b608dia/2+.5])
        rotate([0,90,0])
        cylinder(d=8,h=actw+2,$fn=32,center=true);
    translate([ 0,-(b608dia/2+4)-5-disty/2-dyoff-disty/2,b608dia/2+.5])
        rotate([0,90,0])
        cylinder(d=8,h=actw+2,$fn=32,center=true);


    translate([ 0,-(b608dia/2+4)-5-dyoff-disty/2,-1]){
        translate([-(actw-myd)/2,-(disty/2+myd),0])
        cylinder(d=2.5,h=b608dia+2,$fn=128,center=false);  
        translate([-(actw-myd)/2, (disty/2+myd),0])
        cylinder(d=2.5,h=b608dia+2,$fn=128,center=false);  
        translate([ (actw-myd)/2,-(disty/2+myd),0])
        cylinder(d=2.5,h=b608dia+2,$fn=128,center=false);  
        translate([ (actw-myd)/2, (disty/2+myd),0])
        cylinder(d=2.5,h=b608dia+2,$fn=128,center=false); 
        translate([-(actw-myd)/2, 0 ,0])
        cylinder(d=2.5,h=b608dia+2,$fn=128,center=false); 
        translate([ (actw-myd)/2, 0 ,0])
        cylinder(d=2.5,h=b608dia+2,$fn=128,center=false); 
    }   
    
    }
}
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

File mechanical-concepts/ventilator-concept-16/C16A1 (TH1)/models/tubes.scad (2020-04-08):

stuetz=0;       //supportmaterial 
cone=0;         //Form cone
brim=0;         //brim for print bed adhesion

fn=32;          //default for $fn

idb=15.25;      //some inner diameter
odb=22.43-.3;   

th=3;           //wall thickness
spiel=.7;       //margin (outlets will be that bigger)


// some diameters for my special parts
t_od=(12.01+12.47)/2;
t_id=8;
d_od=27.6; //od_deckel
d_h=7.84;

//example

adapter(
        35,            //diameter bigger inlet
        15,            //diameter smaller inlet
        30,            //length bigger inlet side
        20,            //length smaller inlet side
        cone=1         //outer conus form
        );
//adapter are closed by a 0.5 mm sheet for printability;
//bore them out in smaller diameter


//translate([0,34,0])adapter(odb,t_od,d_h,15,cone=1); //deckel();
//sensor1(cone=1,stuetz=1,brim=1);
//translate([0,34,0])adapter(odb,t_od,15,15,cone=1,brim=0);   //beutel, Schlauch


module sensor1(){    //special adapter with cable outlet
  difference(){
   adapter(d_od,t_od,d_h,15+8,stuetz=stuetz,cone=cone,brim=brim); 
   translate([0,0,d_h])
      rotate([0,60,0])
      translate([0,0,-4])
      cylinder(d=3,h=200,$fn=fn);
  }
}

module adapter(od1, od2,l,l2){
 
difference(){
      union(){
       if(brim>0){
        cylinder(d=od1+spiel+4*th,h=.5,$fn=fn*2); }
        
        cylinder(d=od1+spiel+2*th,h=l+th,$fn=fn*2);
         if(cone>0){
            translate([0,0,l+th-.1])
                cylinder(d1=od1+spiel+2*th,d2=od2+spiel+2*th,h=od1-od2,$fn=fn*2);     
             
             } 
        translate([0,0,l])
        cylinder(d=od2+spiel+2*th,h=l2,$fn=fn*2); 
          
      }
        translate([0,0,-.1])
        cylinder(d1=od1+spiel+.5,d2=od1+spiel,h=l+.01,$fn=fn*2); 
        translate([0,0,l+.5])
        cylinder(d1=od2+spiel,d2=od2+spiel,h=th,$fn=fn*2); 
        translate([0,0,l+.5])
        cylinder(d1=od2+spiel,d2=od2+spiel+.5,h=l2,$fn=fn*2); 
    translate([0,0,l+l2+.001])
       cylinder(d=od1+od2,h=l+l2);
    }   
    
   if(stuetz>0){
     difference(){
        cylinder(d1=od2+spiel+2,d2=od2+spiel+.5,h=l+.002,$fn=fn*2); 
        translate([0,0,+.5])
        cylinder(d1=od2+spiel,d2=od2+spiel+.5,h=l+.002,$fn=fn*2); 
    }   
       
   }
    
    
}

/////////////////////outdated modules
module deckel(){
d2=27.10;
d1=27.6;
dh=7.84;
difference(){
      union(){
        cylinder(d=d1+spiel+4*th,h=.5,$fn=fn*2); 
        cylinder(d1=d1+spiel+2*th,d2=d2+spiel+2*th,h=dh+th,$fn=fn*2); 
        translate([0,0,dh+.5])
        tube(t_od,20);
      }
        translate([0,0,-.1])
        cylinder(d1=d1+spiel,d2=d2+spiel,h=dh,$fn=fn*2); 
        translate([0,0,dh+.5])
        cylinder(d=t_od,h=dh,$fn=fn*2); 
      
    }    
    
}

module bag1(){
l1=25;    
    
    difference(){
       union(){
        cylinder(d=odb+2*th,h=l1,$fn=fn*2); 
       }       
        translate([0,0,-.1])
        cylinder(d1=odb+spiel+1,d2=odb,h=10,$fn=fn*2); 
        cylinder(d1=odb+spiel+1,d2=odb,h=l1+.2,$fn=fn*2); 
    }
}

module tube(od,l ){
l1=25;    
    
    difference(){
       union(){
        cylinder(d=od+4*th,h=.5,$fn=fn*2); 
        cylinder(d=od+2*th,h=l,$fn=fn*2); 
       }       
        translate([0,0,-.1])
        cylinder(d1=od+spiel+1,d2=od,h=l,$fn=fn*2); 
        cylinder(d1=od+spiel+1,d2=od,h=l+.2,$fn=fn*2); 
    }
}

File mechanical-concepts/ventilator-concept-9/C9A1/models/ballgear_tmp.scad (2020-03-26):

$fn=120;

d=5;
ra=85;
ri=60;
rct=2.5;
offset=150;
difference(){

translate([0,0,-offset])import("/home/knief/Desktop/ballgear.stl");
f=5; //heights factor base
union(){
translate([ra,ra+f*d,0]) rotate([0,0,-135])translate([ra-(ra-ri)/2-3,0,0])cylinder(8,rct,3*rct);
    translate([ra,ra+f*d,0]) rotate([0,0,135])translate([ra-(ra-ri)/2-3,0,0])cylinder(8,rct,3*rct);
    translate([ra,ra+f*d,0]) rotate([0,0,45])translate([ra-(ra-ri)/2-3,0,0])cylinder(8,rct,3*rct);
    translate([ra,ra+f*d,0]) rotate([0,0,-45])translate([ra-(ra-ri)/2-3,0,0])cylinder(8,rct,3*rct);

//translate([d*f,0,-5])cube([15,15,172]);    
//translate([(2*ra)-(d*f)-3*d,0,-5])cube([15,15,172]);
}
}

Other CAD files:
mechanical-concepts/ventilator-concept-13/C13A1 (Jaws)/models/OSV Velocity - Jaws concept/r_000_4_1_2020/R_100_ASM.sldasm
mechanical-concepts/ventilator-concept-15/C15A1/CXI-A-0001.SLDASM
mechanical-concepts/ventilator-concept-9/C9A1/models/Wringer_2.scad
control-electronics/Electronic-Modules/Sensors/Sensors-3D_Models/ms4525-ds-s_p2-54_l17-4_w12-4.igs
control-electronics/Electronic-Modules/Sensors/Sensors-3D_Models/ms4525-ds-s_p2-54_l17-4_w12-4.stp
control-electronics/Electronic-Modules/User_Interface/Rev1_OSV-UserInterface-Velocity-Team/3D-Models/OSV-UserInterface.step
control-electronics/Electronic-Modules/User_Interface/Rev1_OSV-UserInterface-Velocity-Team/3D-Models/Push-button_D6C60F2LFS.stp
mechanical-concepts/_retired-concepts/ventilator-concept-1/concept-1-arm.stl
mechanical-concepts/_retired-concepts/ventilator-concept-1/concept-1-assembly.stp
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

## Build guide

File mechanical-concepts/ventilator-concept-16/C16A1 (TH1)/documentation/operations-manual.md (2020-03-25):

# Emergency Mechanical Ventilator Operations Manual

> **THIS DOCUMENT IS AN EARLY DRAFT AND NOT FOR REFERENCE IN A MEDICAL SETTING.**
> 
> This **DRAFT** document assumes a ventilator design which meets the "Indicative Specification for a Rapidly Manufactured Ventilation System", as published by the [British Chamber of Commerce](https://www.britishchambers.org.uk/media/get/Specification%20For%20RMVS%20Challenge.pdf).
>
> Prior to publication for use in the field, this document will be revised to conform to the final emergency ventilator design, appearance and specifications. Such revisions will include images of the actual ventilator, a table of contents, contact information, etc. All editing comments (shown in the same blue as this text) will be removed from any final revisions. Final revisions of this document will be subjected to review for technical accuracy by (1) an engineer familiar with the final product requirements, design, components and method of construction, and (2) a medical professional certified in the use of mechanical ventilators for respiratory care.

## Intended Use

This mechanical ventilator is intended only for emergency situations where a commercial, medical-grade mechanical ventilator is unavailable. Only trained medical personnel are to use this ventilator for patient care. Serious harm or death to the patient or care providers may result from improper use or from failing to abide by the Requirements, Restrictions and Precautions, below.

### Non-Standard Testing and Certification

This ventilator was designed in a crash program to devise an inexpensive and locally buildable ventilator to respond to the COVID-19 pandemic. Neither the design nor the final product have been through normal quality control or certification processes.

This Emergency Mechanical Ventilator’s individual components, as specified in the `_______` Emergency Mechanical Ventilator Parts List, Construction and Assembly Instruction Set, Revision `_______`, have been through the following testing and certification processes:

Motor: Manufactured by `_____________` with ISO `____` certification *[assumption]*, having a duty cycle of `____`% `_____` continuous.

Bag Valve (air bladder): `_______________`

Pneumatic Valves: `___________________`

Electronic Components: `_______________`

Similar Emergency Mechanical Ventilator units as a whole have been built from the `_______` Emergency Mechanical Ventilator Parts List, Construction and Assembly Instruction Set, Revision `_______` and then subjected to the following informal testing processes:

`____________________`

`____________________`

> **Note:** The ventilator may lack redundancy and other safety features found on commercially manufactured medical-grade mechanical ventilators.

## Requirements, Restrictions and Precautions

**Supervision:** medical staff must remain close enough to the ventilator at all times so that any audible alarm can be heard and responded to. Such medical staff must have the training and ability to detach the ventilator from the patient and replace it with a spare unit or manual bag valve should the unit fail for any reason.

**Basic Safety:** Keep the unit away from excessive humidity levels, flammable gases and hazardous chemicals. Exercise the same precautions as with any electric device.

**Pathogen Risk:** pathogens carried as aerosols in the patients exhalations may be exhausted from the unit during operation. *Medical staff must use N95 masks to protect themselves.* An optional HEPA filter can provide additional protection against pathogens.

**Duty Cycle:** 100% for 14 days continuous.

* The ventilator must not be run for longer than 14 days (336 hours) cumulative in total &mdash; whether continuous or discontinuous.

* The ventilator must be decommissioned (and optionally refurbished) after the equivalent of 14 days of cumulative operation (336 hours).

A simple digital watch with a stopwatch/timer feature can be used to track cumulative run time (run times should be noted in a paper log book to accompany the ventilator).

**Power requirements:** (see Specifications)

**Operating Environment:** the Emergency Mechanical Ventilator is designed for indoor use, where the unit can be placed horizontally on its base and where extremes of humidity, temperature, vibration and dust can be avoided.

### Controls and Operation

It is assumed that the operator is a trained medical professional with experience in the use of mechanical ventilators. It is beyond the scope of this manual to cover respiratory care, intubation, patient positioning and monitoring requirements, etc.

> A note should be included here to describe
> * the mode(s) of mechanical ventilation offered by this unit, .i.e. Volume Cycled, SIMV, Pressure Control Ventilation, Pressure Support Ventilation, etc.
> * whether breaths are strictly timed or triggered by the patient
> * whether pressure is fixed or adjustable &mdash; as defined in the [Merck Manual](https://www.merckmanuals.com/professional/critical-care-medicine/respiratory-failure-and-mechanical-ventilation/overview-of-mechanical-ventilation).

The Emergency Mechanical Ventilator offers a few basic controls and features, as shown in the image below:

**Volume Knob:** adjust the volume of air or oxygen delivered to the patient with each inhalation cycle. Volume should be set according to standard practice for ventilation of a patient. Volume settings are typically 350 ml per breath or 450 ml per breath, depending on the patient.

* *[Does ventilator have the ability to show actual volume via gauges/sensors?]*
* *[Does unit need to be calibrated to ensure accurate volume settings?]*
* *[Should this control offer fixed positions for specific pressures?]*

**Note:** the patient inhalation supply pipework will remain pressurised at all times to maintain PEEP pressure at 150mm H₂0 *[Assumed per RMVS specifications. Need to know if this requires a switch to turn on/off]*.

**Breaths Per Minute (BPM) Knob:** adjustable rate of between 12 and 20 cycles/breaths per minute. Rate set according to the specific patient’s needs; may require periodic manual adjustment.

**Inspiratory/Expiratory (I/E) Ratio Knob:** adjust the relative duration of the inhalation cycle and the exhalation cycle. Ratio set according to the specific patient’s needs; may require periodic manual adjustment.

**(Optional) Digital Display:** Shows the current settings for Volume, Breaths Per Minute and I/E.

**(Optional) Pressure Relief Valve:** Ensure air pressure to the patient (high pressure) never exceeds 350 mm H₂O.

**Inspiratory Connection Port:** connection point for flexible tubing leading to the patient.

**Oxygen Port:** connection point for oxygen tank to supply oxygen to the patient.

**(Optional) Oxygen Mix Valve:** Adjust the concentration of oxygen to air in the gas mixture supplied to the patient. Assumes O2 supplied at `_____` pressure. *[assumption that a mix valve is a valid option]*.

> **NOTE:** No alarm is provided to alert if the oxygen supply diminishes *[assumption]*.

**Expiratory Connection Port:** connection point for flexible tubing leading from the patient.

**Expiratory Exhaust Port:** exhausts exhalation from the patient to the environment, optionally through a HEPA filter attachment.

**(Optional) HEPA filter for expiratory output port:** Minimizes the spread of viruses or other pathogens from the patient (via aerosols) to the immediate environment &mdash; for the welfare of nearby medical staff or anyone else nearby who is not already suffering from the same respiratory infection(s) as the patient. 

> **NOTE:** N95 face masks (or equivalent) must be worn by all medical staff in proximity to the patient or the ventilator even if the ventilator is equipped with a HEPA filter.

The HEPA filter (and the ventilator itself) must be replaced after a cumulative run-time of 14 days (336 hours). In a field hospital setting with dusty conditions, the HEPA filter may need to be replaced prior to the decommissioning of the ventilator. Note that ventilator run time must be logged in a log book which accompanies the ventilator.

**(Optional) Pressure Loss Alarm:** Audible alarm sounds when unit is powered on and pressure falls below `____` mm H₂O on the inhalation line for any reason.

### Cleaning, Sanitation and Maintenance

Do not clean a ventilator actively being used by a patient.

Unplug the ventilator before attempting to clean it.

The ventilator exterior can be cleaned with a paper towel lightly dampened with isopropyl alcohol. 

Do not get the ventilator wet.

The ventilator’s motor(s) should not be cleaned or lubricated. Rather, the motor(s) should be refurbished after the ventilator reaches the end of its duty cycle of 14 days (336 hours of cumulative operation).

The ventilator’s inflatable bag and flex lines which make up the inhalation line should be replaced if the ventilator needs to be connected to a different patient.

The ventilator’s inflatable bag and flex lines which make up the inhalation line could possibly be disconnected from the ventilator and sanitized, provided these components are capable of withstanding the temperatures needed for sanitation. 

Refer to product documentation for the inflatable bag and ventilation valves and flex lines *[need to validate]*.

Ventilator run time must be logged in a log book which accompanies the ventilator, to ensure the ventilator does not exceed its duty cycle of 14 days (336) hours of cumulative run-time (whether continuous or intermittent).

### Specifications

Power requirements:

Volts A/C: `____` *[assuming A/C]*

Watts: `_____`

Duty Cycle: 100% continuous for 14 days (336 hours)

Volume accuracy: +/- 10 ml per breath @ 350 ml/breath or 450 ml/breath

Breath Frequency Accuracy: within 1 breath per minute.

Audible alarm volume (dB): `_____`

These specifications are subject to change. Duty cycle may be lengthened as more testing data accumulates.

### Obtaining Assistance

Contact `_________________` for support.

Register this product online at `_________________` to receive any notifications or gain access to additional documentation including:

* Safety recalls (due to design or components).
* New options.
* Possible duty cycle extensions.
* Refurbishing procedures.
* Revisions to or translations of this operations manual or specifications.
* Spare parts availability.
* Refinements to the design.
* Parts lists, build and assembly instructions.

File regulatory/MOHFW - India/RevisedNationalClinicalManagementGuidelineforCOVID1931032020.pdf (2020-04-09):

Government of India
Ministry of Health & Family Welfare Directorate General of Health Services (EMR Division)

# Revised Guidelines on Clinical Management of COVID – 19

This document is intended for clinicians taking care of hospitalised adult and paediatric patients of COVID – 19. It is not meant to replace clinical judgment or specialist consultation but rather to strengthen clinical management of these patients and provide to up-to-date guidance. Best practices for COVID - 19 including IPC and optimized supportive care for severely ill patients as considered essential. This document aims to provide clinicians with updated interim guidance on timely, effective, and safe supportive management of patients with COVID - 19, particularly those with severe acute respiratory illness and critically ill.

31

st March 2020

## TABLE OF CONTENTS

No. | Topic | Page No.
1 | Case definitions | 1
2 | Clinical features | 2
3 | Immediate implementation of IPC measures | 4
4 | Laboratory diagnosis | 6
5 | Early supporting therapy and monitoring | 8
6 Management of hypoxemic respiratory failure | and ARDS | 10
7 | Management of septic shock | 13
8 | Other therapeutic measures | 15
9 | Prevention of complications | 16
10 | Specific therapy | 18

When to suspect

- All symptomatic individuals who have undertaken international travel in the last 14 days

or

- All symptomatic contacts of laboratory confirmed cases

or

- All symptomatic healthcare personnel (HCP)

or

- All hospitalized patients with severe acute respiratory illness ( SARI) (fever AND

cough and/or shortness of breath)

or

- Asymptomatic direct and high risk contacts of a confirmed case (should be tested once

between day 5 and day 14 after contact)

Symptomatic refers to fever/cough/shortness of breath.

Direct and high-risk contacts include those who live in the same household with a confirmed

case and HCP who examined a confirmed case.

## 1. Case definition

Confirmed case

A person with laboratory confirmation of COVID-19 infection, irrespective of clinical signs and

symptoms

## 2. Clinical features

COVID–19 may present with mild, moderate, or severe illness; the latter includes severe

pneumonia, ARDS, sepsis and septic shock. Early recognition of suspected patients allows for

timely initiation of IPC (see Table 1). Early identification of those with severe manifestations (see

Table 1) allows for immediate optimized supportive care treatments and safe, rapid admission (or

referral) to intensive care unit .

Table 1: Clinical syndromes associated with COVID - 19 infection

Uncomplicated illness | Patients with uncomplicated upper respiratory tract viral infection, may have non-specific symptoms such as fever, cough, sore throat, nasal congestion, malaise, headache. The elderly and immunosuppressed may present with atypical symptoms.
Mild pneumonia | Patient with pneumonia and no signs of severe pneumonia. Child with non-severe pneumonia has cough or difficulty in breathing/ fast breathing: (fast breathing - in breaths/min): <2 months, ≥60; 2–11 months, ≥50; 1– 5 years, ≥40 and no signs of severe pneumonia

Severe

pneumonia

Adolescent or adult: fever or suspected respiratory infection, plus one of the

following; respiratory rate >30 breaths/min, severe respiratory distress, SpO2 <90%

on room air

Child with cough or difficulty in breathing, plus at least one of the following: central

cyanosis or SpO2 <90%; severe respiratory distress (e.g. grunting, chest in-

drawing); signs of pneumonia with any of the following danger signs: inability to

breastfeed or drink, lethargy or unconsciousness, or convulsions. Other signs of

pneumonia may be present: chest indrawing, fast breathing (in breaths/min): <2

months ≥60; 2–11 months ≥50; 1–5 years ≥40. The diagnosis is clinical; chest

imaging can exclude complications.

Acute

Respiratory

Distress

Syndrome

Onset: new or worsening respiratory symptoms within one week of known clinical

insult.

Chest imaging (radiograph, CT scan, or lung ultrasound): bilateral opacities, not

fully explained by effusions, lobar or lung collapse, or nodules.

Origin of oedema: respiratory failure not fully explained by cardiac failure or fluid

overload. Need objective assessment (e.g. echocardiography) to exclude hydrostatic

cause of oedema if no risk factor present.

Oxygenation (adults):

- Mild ARDS: 200 mmHg < PaO2/FiO2 ≤ 300 mmHg (with PEEP or CPAP ≥5

cm H2O, or non-ventilated)

- Moderate ARDS: 100 mmHg < PaO2/FiO2 ≤200 mmHg with PEEP ≥5 cm H2O,

or non-ventilated)

- Severe ARDS: PaO2/FiO2 ≤ 100 mmHg with PEEP ≥5 cm H2O, or non-

ventilated)

- When PaO2 is not available, SpO2/FiO2 ≤315 suggests ARDS (including innon-

ventilated patients)

Oxygenation (children; note OI = Oxygenation Index and OSI = Oxygenation Index

using SpO2)

- Bilevel NIV or CPAP ≥5 cm H2O via full face mask: PaO2/FiO2 ≤ 300 mmHg

or SpO2/FiO2 ≤264

- Mild ARDS (invasively ventilated): 4 ≤ OI < 8 or 5 ≤ OSI < 7.5
- Moderate ARDS (invasively ventilated): 8 ≤ OI < 16 or 7.5 ≤ OSI < 12.3
- Severe ARDS (invasively ventilated): OI ≥ 16 or OSI ≥ 12.3
Sepsis | Adults: life-threatening organ dysfunction caused by a dysregulated host response to suspected or proven infection, with organ dysfunction. Signs of organ dysfunction include: altered mental status, difficult or fast breathing, low oxygen saturation, reduced urine output, fast heart rate, weak pulse, cold extremities or low blood pressure, skin mottling, or laboratory evidence of coagulopathy, thrombocytopenia, acidosis, high lactate or hyperbilirubinemia. Children: suspected or proven infection and ≥2 SIRS criteria, of which one must be abnormal temperature or white blood cell count
Septic Shock | Adults: persisting hypotension despite volume resuscitation, requiring vasopressors to maintain MAP ≥65 mmHg and serum lactate level < 2 mmol/L Children: any hypotension (SBP <5th centile or >2 SD below normal for age) or 2-3 of the following: altered mental state; bradycardia or tachycardia (HR <90 bpm or >160 bpm in infants and HR <70 bpm or >150 bpm in children); prolonged capillary refill (>2 sec) or warm vasodilation with bounding pulses; tachypnea;

mottled skin or petechial or purpuric rash; increased lactate; oliguria; hyperthermia

or hypothermia

## 3. Immediate implementation of appropriate IPC measures

Infection prevention control (IPC) is a critical and integral part of clinical management of patients

and should be initiated at the point of entry of the patient to hospital (typically the Emergency

Department). Standard precautions should always be routinely applied in all areas of health care

facilities. Standard precautions include hand hygiene; use of PPE to avoid direct contact with

patients’ blood, body fluids, secretions (including respiratory secretions) and non-intact skin.

Standard precautions also include prevention of needle-stick or sharps injury; safe waste

management; cleaning and disinfection of equipment; and cleaning of the environment.

Table 2: How to implement infection prevention and control measures for patients with suspected or confirmed COVID - 19 infection
At triage
- Give suspect patient a triple layer surgical mask and direct patient to separate

area, an isolation room if available. Keep at least 1meter distance between

suspected patients and other patients. Instruct all patients to cover nose and

mouth during coughing or sneezing with tissue or flexed elbow for others.

Perform hand hygiene after contact with respiratory secretions

Apply droplet
precautions | • | Droplet precautions prevent large droplet transmission of respiratory viruses.
| | Use a triple layer surgical mask if working within 1-2 metres of the patient.
| | Place patients in single rooms, or group together those with the same etiological
| | diagnosis. If an etiological diagnosis is not possible, group patients with similar
| | clinical diagnosis and based on epidemiological risk factors, with a spatial
| | separation. When providing care in close contact with a patient with respiratory
| | symptoms (e.g. coughing or sneezing), use eye protection (face-mask or
| | goggles), because sprays of secretions may occur. Limit patient movement
| | within the institution and ensure that patients wear triple layer surgical masks
| | when outside their rooms

Apply contact
precautions | • | Droplet and contact precautions prevent direct or indirect transmission from

contact with contaminated surfaces or equipment (i.e. contact with

contaminated oxygen tubing/interfaces). Use PPE (triple layer surgical mask,

eye protection, gloves and gown) when entering room and remove PPE when

leaving. If possible, use either disposable or dedicated equipment (e.g.

stethoscopes, blood pressure cuffs and thermometers). If equipment needs to

be shared among patients, clean and disinfect between each patient use. Ensure

that health care workers refrain from touching their eyes, nose, and mouth with

potentially contaminated gloved or ungloved hands. Avoid contaminating

environmental surfaces that are not directly related to patient care (e.g. door

handles and light switches). Ensure adequate room ventilation. Avoid

movement of patients or transport. Perform hand hygiene.

Apply airborne
precautions
when
performing an
aerosol
generating
procedure
- Ensure that healthcare workers performing aerosol-generating procedures (i.e.
open | suctioning | of | respiratory | tract, | intubation, | bronchoscopy,

cardiopulmonary resuscitation) use PPE, including gloves, long-sleeved

gowns, eye protection, and fit-tested particulate respirators (N95). (The

scheduled fit test should not be confused with user seal check before each use.)

Whenever possible, use adequately ventilated single rooms when performing

aerosol-generating procedures, meaning negative pressure rooms with

minimum of 12 air changes per hour or at least 160 litres/second/patient in

facilities with natural ventilation. Avoid the presence of unnecessary

individuals in the room. Care for the patient in the same type of room after

mechanical ventilation commences

Abbreviations: ARI, acute respiratory infection; PPE, personal protective equipment

## 4. Laboratory diagnosis

Guidance on specimen collection, processing, transportation, including related biosafety

procedures, is available on https://mohfw.gov.in/media/disease-alerts.

As per directive from MoHFW, Government of India, all suspected cases are to be reported to

district and state surveillance officers.

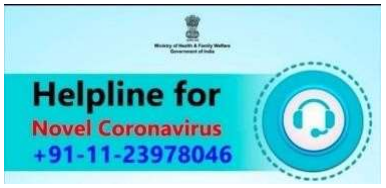
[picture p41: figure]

Figure 1: Helpline for COVID-19 (MOHFW, GOI)

Sample collection:

Preferred sample: Throat and nasal swab in viral transport media (VTM) and transported on ice

Alternate: Nasopharyngeal swab, BAL or endotracheal aspirate which has to be mixed with the

viral transport medium and transported on ice

General guidelines:

- Trained health care professionals to wear appropriate PPE with latex free purple nitrile

gloves while collecting the sample from the patient. Maintain proper infection

control (https://www.cdc.gov/infectioncontrol/guidelines/isolation/index.html#a4) when collecting specimens

- Restricted entry to visitors or attendants during sample collection
- Complete the requisition form for each specimen submitted
- Proper disposal of all waste generated

Respiratory specimen collection methods:

A. Lower respiratory tract
- Bronchoalveolar lavage, tracheal aspirate, sputum
- Collect 2-3 mL into a sterile, leak-proof, screw-cap sputum collection cup or sterile

dry container.

B. Upper respiratory tract
- Nasopharyngeal swab AND oropharyngeal swab

Oropharyngeal swab (e.g. throat swab): Tilt patient’s head back 70 degrees. Rub swab over

both tonsillar pillars and posterior oropharynx and avoid touching the tongue, teeth, and

gums. Use only synthetic fiberswabs with plastic shafts. Do not use calcium alginate swabs

or swabs with wooden shafts. Place swabs immediately into sterile tubes containing 2-3 ml

of viral transport media.

Combined nasal & throat swab: Tilt patient’s head back 70 degrees. While gently rotating

the swab, insert swab less than one inch into nostril (until resistance is met at turbinates).

Rotate the swab several times against nasal wall and repeat in other nostril using the same

swab. Place tip of the swab into sterile viral transport media tube and cut off the applicator

stick. For throat swab, take a second dry polyester swab, insert into mouth, and swab the

posterior pharynx and tonsillar areas (avoid the tongue). Place tip of swab into the same

tube and cut off the applicator tip.

Nasopharyngeal swab: Tilt patient’s head back 70 degrees. Insert flexible swab through the

nares parallel to the palate (not upwards) until resistance is encountered or the distance is

equivalent to that from the ear to the nostril of the patient. Gently, rub and roll the swab.

Leave the swab in place for several seconds to absorb secretions before removing.

Clinicians may also collect lower respiratory tract samples when these are readily available

(for example, in mechanically ventilated patients). In hospitalized patients with confirmed

COVID - 19 infection, repeat upper respiratory tract samples should be collected to

demonstrate viral clearance.

## 5. Early supportive therapy and monitoring

a. Give supplemental oxygen therapy immediately to patients with SARI and respiratory distress,

hypoxaemia, or shock: Initiate oxygen therapy at 5 L/min and titrate flow rates to reach target

SpO2 ≥90% in non-pregnant adults and SpO2 ≥92-95 % in pregnant patients. Children with

emergency signs (obstructed or absent breathing, severe respiratory distress, central cyanosis,

shock, coma or convulsions) should receive oxygen therapy during resuscitation to target SpO2

≥94%; otherwise, the target SpO2 is ≥90%. All areas where patients with SARI are cared for

should be equipped with pulse oximeters, functioning oxygen systems and disposable, single-

use, oxygen-delivering interfaces (nasal cannula, simple face mask, and mask with reservoir

bag). Use contact precautions when handling contaminated oxygen interfaces of patients with

COVID – 19.

b. Use conservative fluid management in patients with SARI when there is no evidence of shock:

Patients with SARI should be treated cautiously with intravenous fluids, because aggressive

fluid resuscitation may worsen oxygenation, especially in settings where there is limited

availability of mechanical ventilation.

c. Give empiric antimicrobials to treat all likely pathogens causing SARI. Give antimicrobials

within one hour of initial patient assessment for patients with sepsis: Although the patient may

be suspected to have COVID - 19, Administer appropriate empiric antimicrobials within ONE

hour of identification of sepsis. Empirical antibiotic treatment should be based on the clinical

diagnosis (community-acquired pneumonia, health care-associated pneumonia [if infection

was acquired in healthcare setting], or sepsis), local epidemiology and susceptibility data, and

treatment guidelines. Empirical therapy includes a neuraminidase inhibitor for treatment of

influenza when there is local circulation or other risk factors, including travel history or

exposure to animal influenza viruses. Empirical therapy should be de-escalated on the basis

of microbiology results and clinical judgment

d. Do not routinely give systemic corticosteroids for treatment of viral pneumonia or ARDS

outside of clinical trials unless they are indicated for another reason: A systematic review of

observational studies of corticosteroids administered to patients with SARS reported no

survival benefit and possible harms (avascular necrosis, psychosis, diabetes, and delayedviral

clearance). A systematic review of observational studies in influenza found a higher risk of

mortality and secondary infections with corticosteroids; the evidence was judged as very low to low quality due to confounding by indication. A subsequent study that addressed this

limitation by adjusting for time-varying confounders found no effect on mortality. Finally, a

recent study of patients receiving corticosteroids for MERS used a similar statistical approach

and found no effect of corticosteroids on mortality but delayed lower respiratory tract (LRT)

clearance of MERS-CoV. Given lack of effectiveness and possible harm, routine

corticosteroids should be avoided unless they are indicated for another reason. See section F

for the use of corticosteroids in sepsis.

e. Closely monitor patients with SARI for signs of clinical deterioration, such as rapidly

progressive respiratory failure and sepsis, and apply supportive care interventions

immediately: Application of timely, effective, and safe supportive therapies is the cornerstone

of therapy for patients that develop severe manifestations of COVID – 19.

f. Understand the patient’s co-morbid condition(s) to tailor the management of critical illness

and appreciate the prognosis: During intensive care management of SARI, determine which

chronic therapies should be continued and which therapies should be stopped temporarily.

g. Communicate early with patient and family: Communicate pro-actively with patients and

families and provide support and prognostic information. Understand the patient’s values and

preferences regarding life-sustaining interventions.

## 6. Management of hypoxemic respiratory failure and ARDS

- Recognize severe hypoxemic respiratory failure when a patient with respiratory distress is

failing standard oxygen therapy. Patients may continue to have increased work of breathing or

hypoxemia even when oxygen is delivered via a face mask with reservoir bag (flow rates of

10-15 L/min, which is typically the minimum flow required to maintain bag inflation; FiO2

0.60-0.95). Hypoxemic respiratory failure in ARDS commonly results from intrapulmonary

ventilation-perfusion mismatch or shunt and usually requires mechanical ventilation.

- High – flow nasal catheter oxygenation or non – invasive mechanical ventilation: When

respiratory distress and/or hypoxemia of the patient cannot be alleviated after receiving

standard oxygen therapy, high – flow nasal cannula oxygen therapy or non – invasive

ventilation can be considered. If conditions do not improve or even get worse within a short

time (1 – 2 hours), tracheal intubation and invasive mechanical ventilation should be used in a

timely manner. Compared to standard oxygen therapy, HFNO reduces the need for intubation.

Patients with hypercapnia (exacerbation of obstructive lung disease, cardiogenic pulmonary

oedema), hemodynamic instability, multi-organ failure, or abnormal mental status should

generally not receive HFNO, although emerging data suggest that HFNO may be safe in patients with mild-moderate and non-worsening hypercapnia²⁵. Patients receiving HFNO

should be in a monitored setting and cared for by experienced personnel capable of

endotracheal intubation in case the patient acutely deteriorates or does not improve after a short

trial (about 1 hr).

- NIV guidelines make no recommendation on use in hypoxemic respiratory failure (apart from

cardiogenic pulmonary oedema and post-operative respiratory failure) or pandemic viral

illness (referring to studies of SARS and pandemic influenza). Risks include delayed

intubation, large tidal volumes, and injurious transpulmonary pressures. Limited data suggest

a high failure rate when MERS patients received NIV. Patients receiving a trial of NIV should

be in a monitored setting and cared for by experienced personnel capable of endotracheal

intubation in case the patient acutely deteriorates or does not improve after a short trial (about

1 hr). Patients with hemodynamic instability, multiorgan failure, or abnormal mental status

should not receive NIV.

- Recent publications suggest that newer HFNO and NIV systems with good interface fitting do

not create widespread dispersion of exhaled air and therefore should be associated with low

risk of airborne transmission.

- Endotracheal intubation should be performed by a trained and experienced provider using

airborne precautions. Patients with ARDS, especially young children or those who are obese

or pregnant, may de-saturate quickly during intubation. Pre-oxygenate with 100% FiO2 for 5

minutes, via a face mask with reservoir bag, bag-valve mask, HFNO, or NIV. Rapid sequence

intubation is appropriate after an airway assessment that identifies no signs of difficult

intubation.

- Implement mechanical ventilation using lower tidal volumes (4–8 ml/kg predicted body

weight, PBW) and lower inspiratory pressures (plateau pressure <30 cmH2O). This is a strong

recommendation from a clinical guideline for patients with ARDS, and is suggested for

patients with sepsis-induced respiratory failure. The initial tidal volume is 6 ml/kg PBW; tidal

volume up to 8 ml/kg PBW is allowed if undesirable side effects occur (e.g. dyssynchrony, pH

<7.15). Hypercapnia is permitted if meeting the pH goal of 7.30-7.45. Ventilator protocols are

available. The use of deep sedation may be required to control respiratory drive and achieve

tidal volume targets.

- In patients with severe ARDS, prone ventilation for >12 hours per day is recommended.

Application of prone ventilation isstrongly recommended for adult and paediatric patients with

severe ARDS but requires sufficient human resources and expertise to be performed safely.

- Use a conservative fluid management strategy for ARDS patients without tissue

hypoperfusion.

- In patients with moderate or severe ARDS, higher PEEP instead of lower PEEP is

suggested.PEEP titration requires consideration of benefits (reducing atelectrauma and

improving alveolar recruitment) vs. risks (end-inspiratory overdistension leading to lung injury

and higher pulmonary vascular resistance). Tables are available to guide PEEP titration based

on the FiO2 required to maintain SpO2. A related intervention of recruitment manoeuvres

(RMs) is delivered as episodic periods of high continuous positive airway pressure [30–40 cm

H2O], progressive incremental increases in PEEP with constant driving pressure, or high

driving pressure; considerations of benefits vs. risks are similar. Higher PEEP and RMs were

both conditionally recommended in a clinical practice guideline. In patients with moderate-severe ARDS (PaO2/FiO2<150), neuromuscular blockade by continuous infusion should not

be routinely used.

- In settings with access to expertise in extracorporeal life support (ECLS), consider referral of

patients with refractory hypoxemia despite lung protective ventilation. ECLS should only be

offered in expert centres with a sufficient case volume to maintain expertise and that can apply

the IPC measures required for COVID – 19 patients

- Avoid disconnecting the patient from the ventilator, which results in loss of PEEP and

atelectasis. Use in-line catheters for airway suctioning and clamp endotracheal tube when

disconnection is required (for example, transfer to a transport ventilator)

## 7. Management of septic shock

- Recognize septic shock in adults when infection is suspected or confirmed AND vasopressors

are needed to maintain mean arterial pressure (MAP) ≥65 mmHg AND lactate is < 2mmol/L,

in absence of hypovolemia. Recognize septic shock in children with any hypotension (systolic

blood pressure [SBP] <5th centile or >2 SD below normal for age) or 2-3 of the following:

altered mental state; tachycardia or bradycardia (HR <90 bpm or >160 bpm in infants and HR

<70 bpm or >150 bpm in children); prolonged capillary refill (>2 sec) or warm vasodilation

with bounding pulses; tachypnea; mottled skin or petechial or purpuric rash; increased lactate;

oliguria; hyperthermia or hypothermia.

- In the absence of a lactate measurement, use MAP and clinical signs of perfusion to define

shock. Standard care includes early recognition and the following treatments within 1 hour of

recognition: antimicrobial therapy and fluid loading and vasopressors for hypotension. The use

of central venous and arterial catheters should be based on resource availability and individual

patient needs. Detailed guidelines are available for the management of septic shock in adults

and children.

- In resuscitation from septic shock in adults, give at least 30 ml/kg of isotonic crystalloid in

adults in the first 3 hours. In resuscitation from septic shock in children in well-resourced

settings, give 20 ml/kg as a rapid bolus and up to 40-60 ml/kg in the first 1 hr. Do not use

hypotonic crystalloids, starches, or gelatins for resuscitation.

- Fluid resuscitation may lead to volume overload, including respiratory failure. If there is no

response to fluid loading and signs of volume overload appear (for example, jugular venous

distension, crackles on lung auscultation, pulmonary oedema on imaging, or hepatomegaly in

children), then reduce or discontinue fluid administration. This step is particularly important

where mechanical ventilation is not available. Alternate fluid regimens are suggested when

caring for children in resource-limited settings.

- Crystalloids include normal saline and Ringer’s lactate. Determine need for additional fluid

boluses (250-1000 ml in adults or 10-20 ml/kg in children) based on clinical response and

improvement of perfusion targets. Perfusion targets include MAP (>65 mmHg or age-

appropriate targets in children), urine output (>0.5 ml/kg/hr in adults, 1 ml/kg/hr in children),

and improvement ofskin mottling, capillary refill, level of consciousness, and lactate. Consider dynamic indices of volume responsiveness to guide volume administration beyond initial

resuscitation based on local resources and experience. These indices include passive leg raises,

fluid challenges with serial stroke volume measurements, or variations in systolic pressure,

pulse pressure, inferior vena cava size, or stroke volume in response to changes in intrathoracic

pressure during mechanical ventilation.

- Administer vasopressors when shock persists during or after fluid resuscitation. The

initial blood pressure target is MAP ≥65 mmHg in adults and age-appropriate targetsin

children.

- If central venous catheters are not available, vasopressors can be given through a peripheral

IV, but use a large vein and closely monitor for signs of extravasation and local tissue necrosis.

If extravasation occurs, stop infusion. Vasopressors can also be administered through

intraosseous needles.

- If signs of poor perfusion and cardiac dysfunction persist despite achieving MAP target with

fluids and vasopressors, consider an inotrope such as dobutamine

## 8. Other therapeutic measures:

For patients with progressive deterioration of oxygenation indicators, rapid worsening on imaging

and excessive activation of the body’s inflammatory response, glucocorticoids can be used for a

short period of time (3 to 5 days). It is recommended that dose should not exceed the equivalent

of methylprednisolone 1 – 2mg/kg/day. Note that a larger dose of glucocorticoid will delay the

removal of coronavirus due to immunosuppressive effects. For pregnant severe and critical cases,

pregnancy should be preferably terminated. Consultations with obstetric, neonatal, and intensive

care specialists (depending on the condition of the mother) are essential. Patients often suffer from

anxiety and fear and they should be supported by psychological counseling.

## 9. Prevention of complications

Implement the following interventions (Table 3) to prevent complications associated with critical

illness. These interventions are based on Surviving Sepsis or other guidelines, and are generally

limited to feasible recommendations based on high quality evidence.

Table 3: Prevention of complications
Anticipated Outcome | Interventions
Reduce days of invasive mechanical ventilation | • Use weaning protocols that include daily assessment for readiness to breathe spontaneously • Minimize continuous or intermittent sedation, targeting specific titration endpoints (light sedation unless contraindicated) or with daily interruption of continuous sedative infusions
Reduce incidence of ventilator associated pneumonia | • Oral intubation is preferable to nasal intubation in adolescents and adults • Keep patient in semi-recumbent position (head of bed elevation 30-45º) • Use a closed suctioning system; periodically drain and discard condensate in tubing • Use a new ventilator circuit for each patient; once patient is ventilated, change circuit if it is soiled or damaged but not routinely • Change heat moisture exchanger when it malfunctions, when soiled, or every 5–7 days
Reduce incidence of venous thromboembolism | • Use pharmacological prophylaxis (low molecular-weight heparin[preferred if available] or heparin 5000 units subcutaneously twice daily) in adolescents and adults without contraindications. For those with contraindications, use mechanical prophylaxis (intermittent pneumatic compression devices).
Reduce incidence of catheter related bloodstream infection | • Use a checklist with completion verified by a real-time observer as reminder of each step needed for sterile insertion and as a daily reminder to remove catheter if no longer needed
Reduce incidence of pressure | • Turn patient every two hours

Ulcers

Reduce incidence of stress ulcers and gastrointestinal bleeding | • Give early enteral nutrition (within 24–48 hours of admission) • Administer histamine-2 receptor blockers or proton-pump inhibitors in patients with risk factors for GI bleeding. Risk factors for gastrointestinal bleeding include mechanical ventilation for ≥48 hours, coagulopathy, renal replacement therapy, liver disease, multiple co-morbidities, and higher organ failure score
Reduce incidence of ICU-related weakness | • Actively mobilize the patient early in the course of illness when safe to do so

## 10. Specific therapy

NO SPECIFIC ANTIVIRALS have been proven to be effective as per currently available data.

However, based on the available information (uncontrolled clinical trials), the following drugs may

be considered as an off – label indication in patients with severe disease and requiring ICU

management:

- Hydroxychloroquine (Dose 400mg BD – for 1 day followed by 200mg BD for 4 days)

In combination with

- Azithromycin (500 mg OD for 5 days)

These drugs should be administered under close medical supervision, with monitoring for side

effects including QTc interval.

The above medication is presently not recommended for children less than 12 years, pregnant

and lactating women.

These guidelines are based on currently available information and would be reviewed from

time to time as new evidence emerges.

Support to Treating Physicians: AIIMS, New Delhi is running a 24x7 helpline to provide

support to the treating physicians on clinical management. The helpline number is

9971876591. The identified nodal doctor of the State, appointed for clinical management of

COVID – 19 should only contact AIIMS Call Centre.

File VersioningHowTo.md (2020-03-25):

## Concepts are versioned by four parts, letter-number-letter-number, defined by regex: [CP]{1}[0-9]+[A-Z][0-9]+

* The first value (letter) designates the concept type (C = mechanical "concept", P = electronic "prototype")
* The second value (number) designates the official concept version.  When a new conceptual model is accepted by the OSV team, it will be granted an incremented concept number.
* The third value (letter) designates a variation of that concept.  These tend to be significant deviations of the concept, but still generally regarded as derivative.
* The forth value (number) designates a minor version change of that model.  Any physical change to the model, no matter how trivial, warrants a minor version change.

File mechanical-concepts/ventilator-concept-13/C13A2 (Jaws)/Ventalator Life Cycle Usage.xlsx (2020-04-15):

Breaths per Minute | 14
Breaths per Hour | 840
Breaths per day | 20160
Breaths per 14 Days | 282240

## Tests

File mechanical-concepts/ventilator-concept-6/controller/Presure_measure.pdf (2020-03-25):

### Pressure Measure

This document studies the use of barometric sensors in pandemic ventilators.
The objective of the pandemic ventilator is to provide the patient with air in adequate conditions (pressure, temperature, flow, O2 concentration, etc.) For this there are some actuators (pumps, blowers, valves, motors). The actuators are controlled by a microcontroller (arduino, ESP32 or other), using the information provided by the sensors (pressure, temperature, flow, others). Doctors adjust respirator parameters and receive information on the patient's situation.

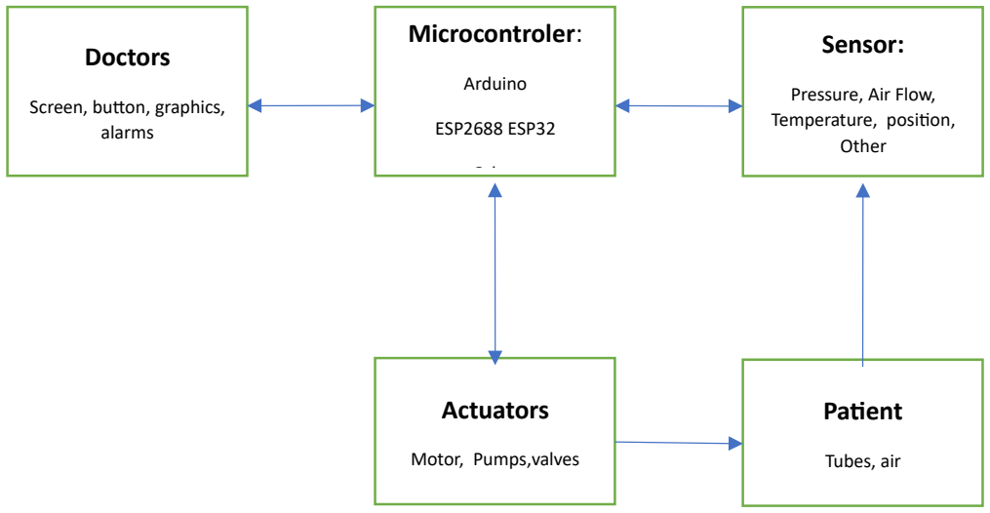
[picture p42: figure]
Microcontroler:; Arduino; ESP2688 ESP32; Sensor:; Pressure, Air Flow, Temperature, position, Other; Actuators; Motor, Pumps,valves; Doctors; Screen, button, graphics, alarms; Patient; Tubes, air

This document will only cover pressure sensors and their integration into the system. Barometric micro electric Mechanci sensors(B-MEMS) measure atmospheric pressure B-MEMS are widely used in smartphones, drones, etc. They are made by millions and cost between € 1 and € 5 and are 2-5mm in size.There are several dozen different Barometric MEMS whose specifications make them suitable for use in Pandemic Ventilators.
The most widely used is the Bosh BMP280. You can buy the sensor for less than €2 from electronic component distributors, or integrated into small PCBs on maker´s Shops.

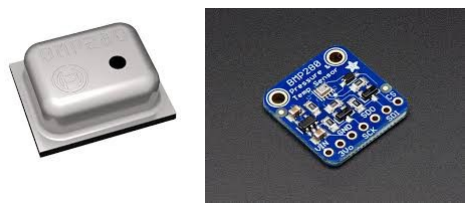
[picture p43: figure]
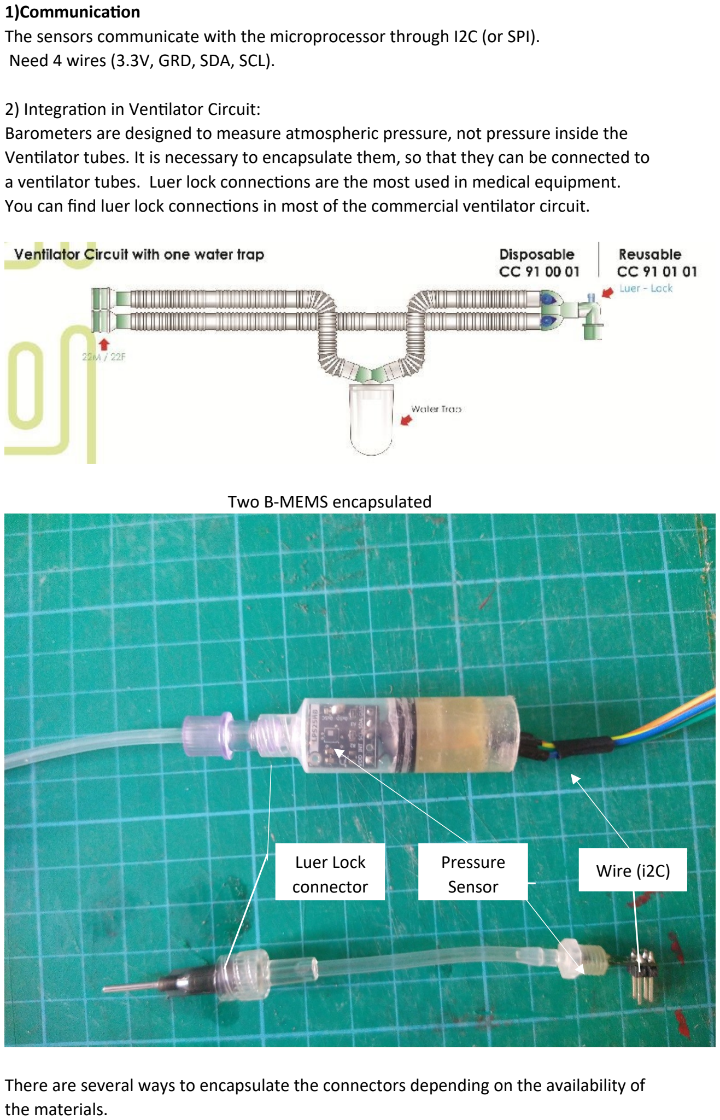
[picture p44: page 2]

1)Communication
The sensors communicate with the microprocessor through I2C (or SPI).
Need 4 wires (3.3V, GRD, SDA, SCL).
2) Integration in Ventilator Circuit:
Barometers are designed to measure atmospheric pressure, not pressure inside the Ventilator tubes. It is necessary to encapsulate them, so that they can be connected to a ventilator tubes. Luer lock connections are the most used in medical equipment. You can find luer lock connections in most of the commercial ventilator circuit.

Two B-MEMS encapsulated

There are several ways to encapsulate the connectors depending on the availability of the materials.

Wire (i2C) Pressure
Sensor

Luer Lock
connector

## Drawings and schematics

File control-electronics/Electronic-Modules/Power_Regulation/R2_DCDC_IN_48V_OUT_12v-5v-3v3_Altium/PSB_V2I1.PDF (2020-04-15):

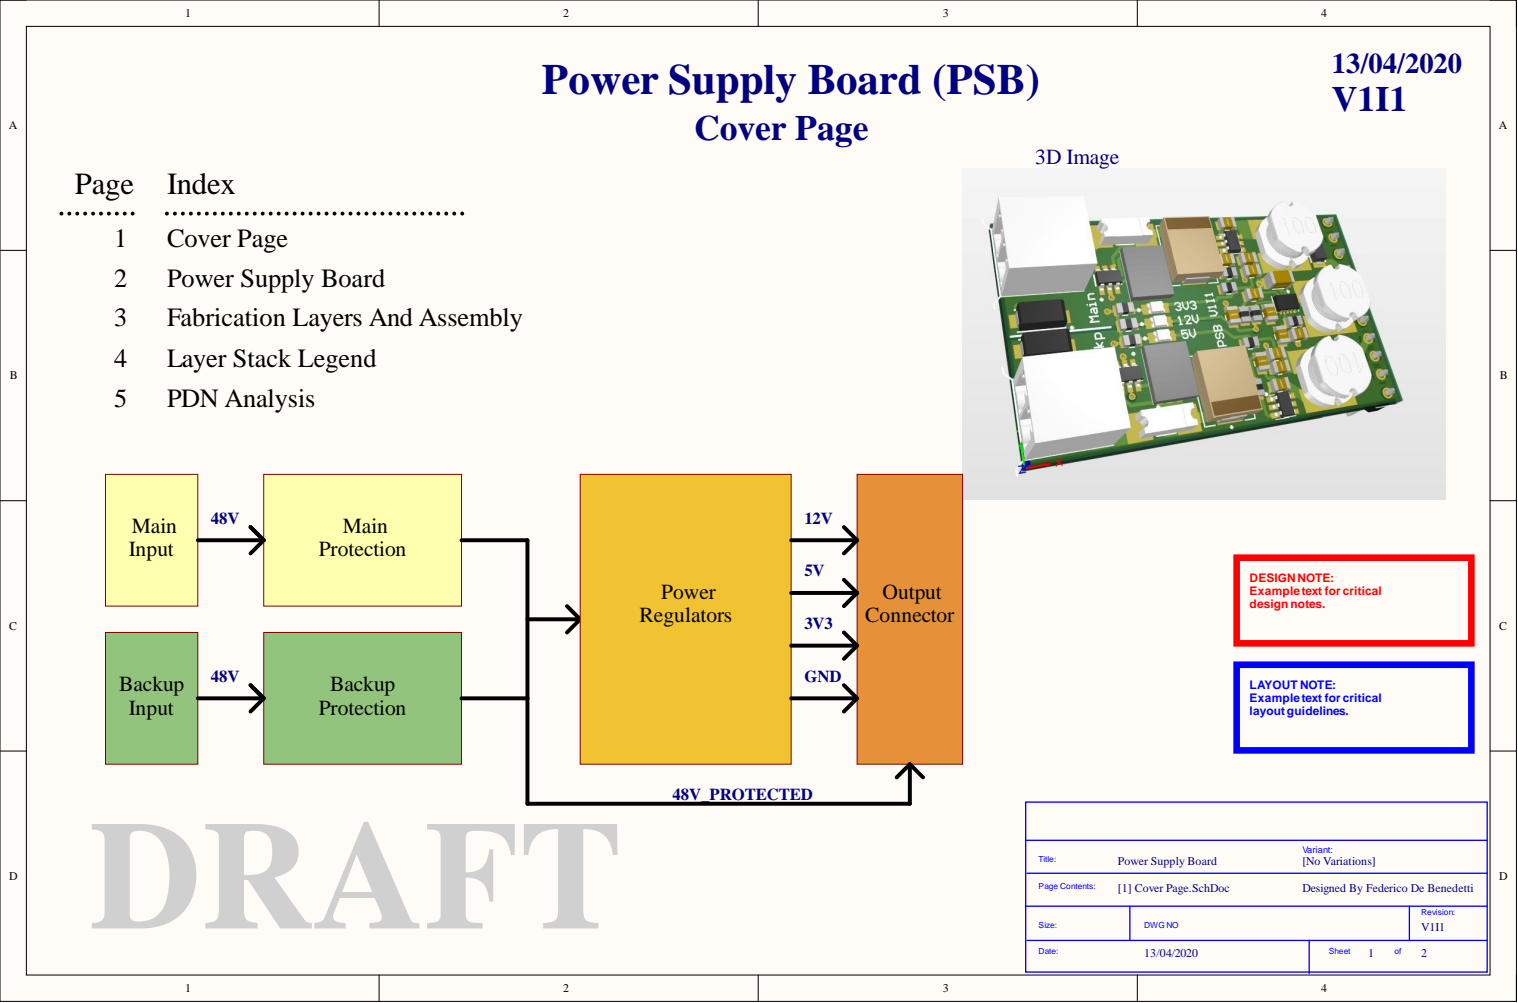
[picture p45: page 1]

Power Supply Board (PSB)

DESIGN NOTE:
Example text for critical
design notes.

LAYOUT NOTE:
layout guidelines.

Designed By Federico De Benedetti

Size: | DWG NO | Revision: V1I1

Date: 13/04/2020 | Sheet of 1 2

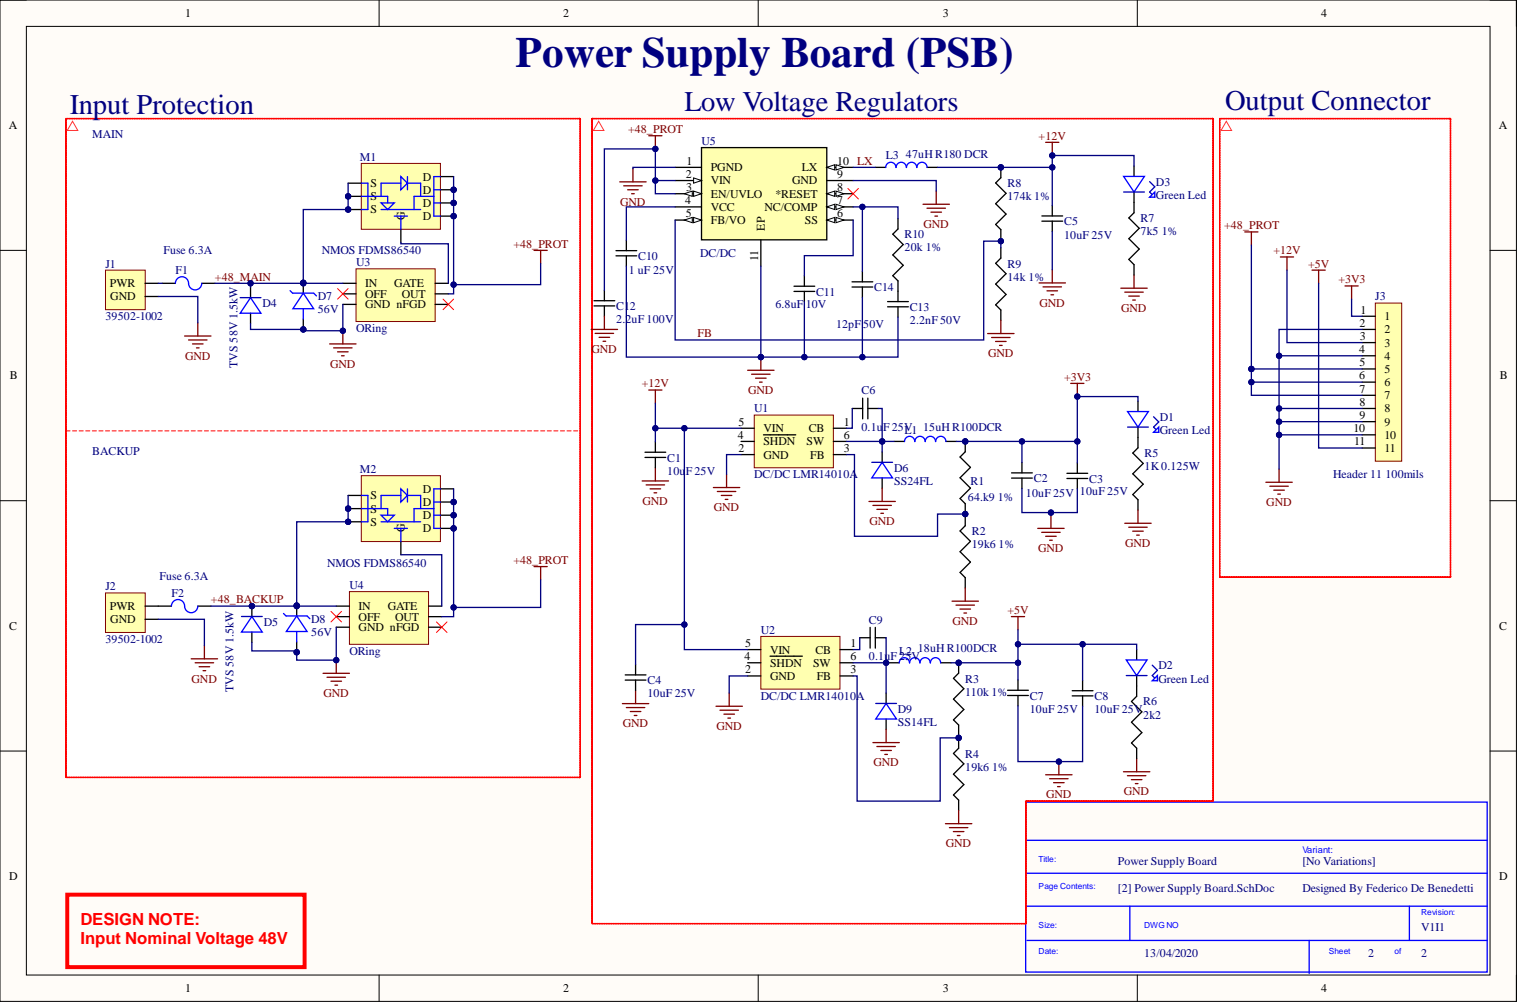
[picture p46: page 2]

Power Supply Board (PSB)

6 6
7 7
8 8
9 9
10 10
11 11

[2] Power Supply Board.SchDoc

Designed By Federico De Benedetti

Size: | DWG NO | Revision: V1I1

Date: 13/04/2020 | Sheet of 2 2

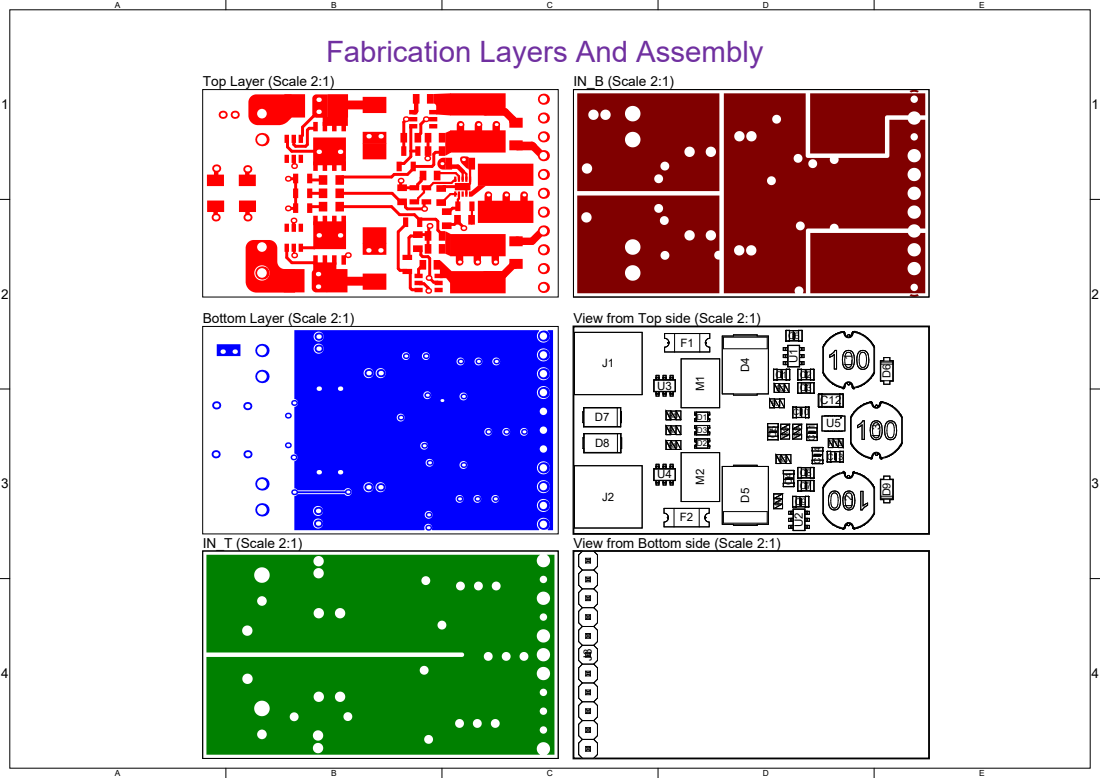
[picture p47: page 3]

Fabrication Layers And Assembly

View from Top side (Scale 2:1) J3

View from Bottom side (Scale 2:1)

1 | 1
2 | 2
3 | 3
4 | 4
Material | Layer | Thickness Dielectric Material Type | Gerber
| Top Overlay | | Legend | GTO
Surface Material Top Solder | 0.01mm | Solder Resist | Solder Mask GTS
Copper | Top Layer | 0.04mm | Signal | GTL
Prepreg | 0.20mm | PP-006 | Dielectric
CF-004 | IN_T | 0.04mm | Internal Plane GP1
Core | 1.03mm | Core-009 | Dielectric
CF-004 | IN_B | 0.04mm | Internal Plane GP2
Prepreg | 0.20mm | PP-006 | Dielectric
Copper | Bottom Layer | 0.04mm | Signal | GBL
Surface Material Bottom Solder 0.01mm | Solder Resist | Solder Mask GBS
| Bottom Overlay | | Legend | GBO

# Total thickness: 1.59mm

# Layer Stack Legend

# Layer Stack Legend

1 | 1
2 | 2
3 | 3
4 | 4

# PDN Analisys

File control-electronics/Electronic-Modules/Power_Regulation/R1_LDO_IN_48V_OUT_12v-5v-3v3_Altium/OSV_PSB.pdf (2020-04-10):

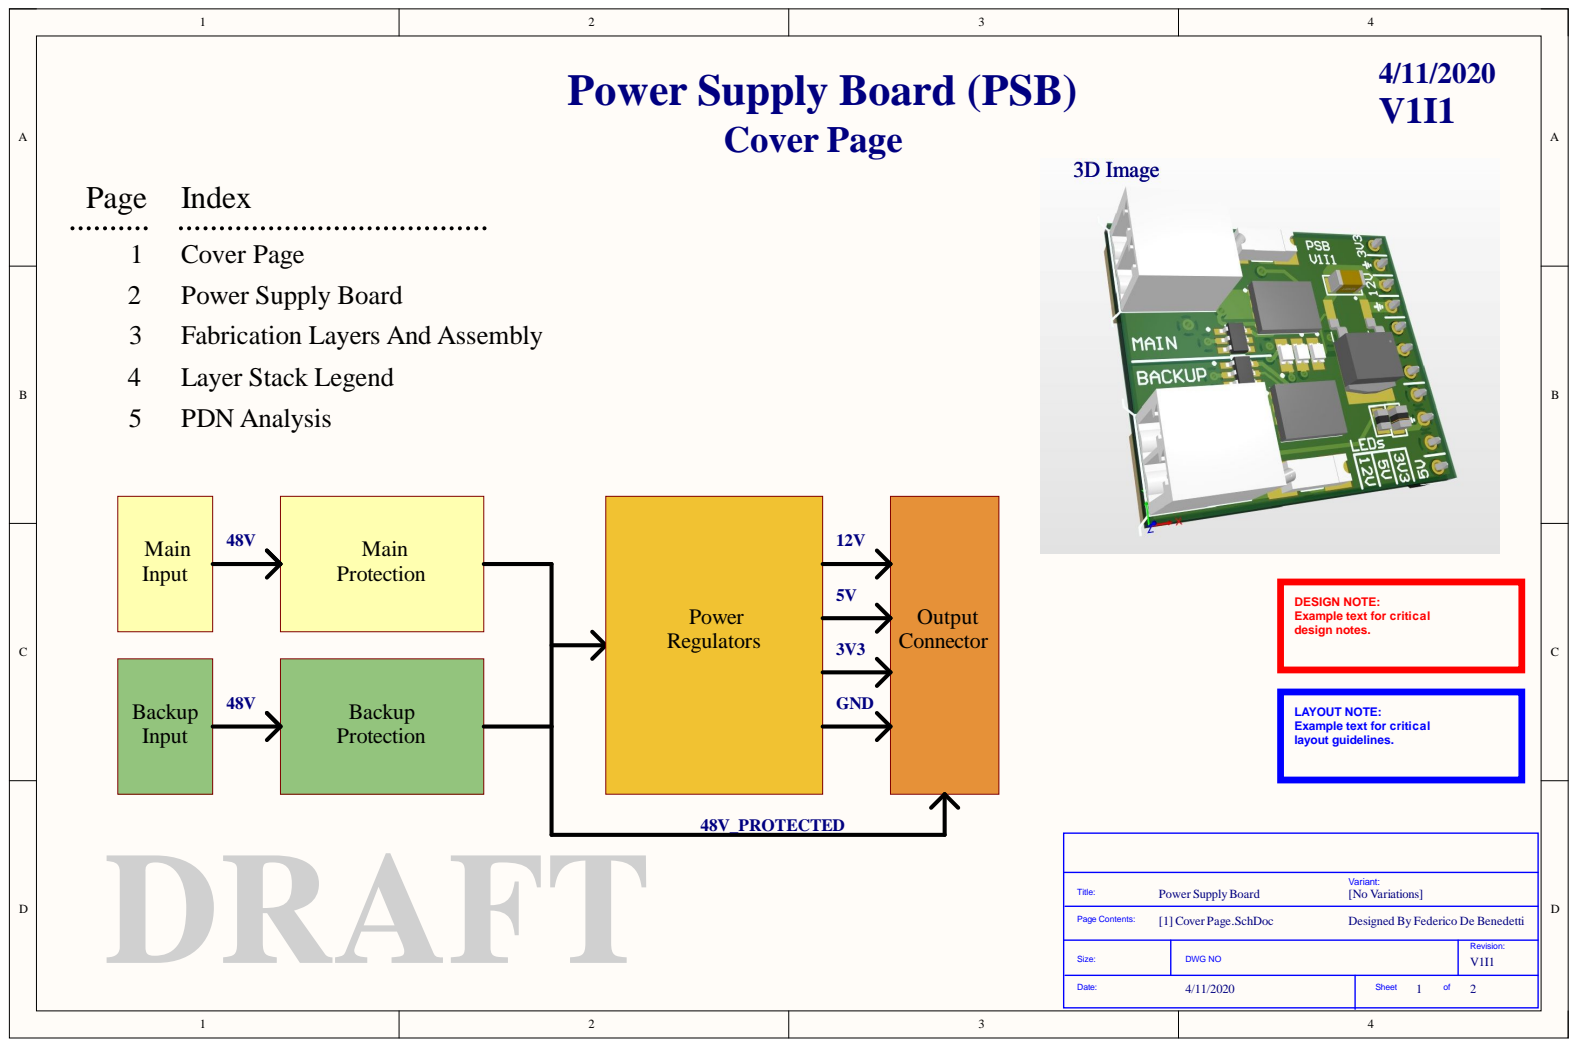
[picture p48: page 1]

Power Supply Board (PSB)

DESIGN NOTE:
Example text for critical
design notes.

LAYOUT NOTE:
layout guidelines.

Designed By Federico De Benedetti

Size: | DWG NO | Revision: V1I1

Date: 4/11/2020 | Sheet 1 of 2

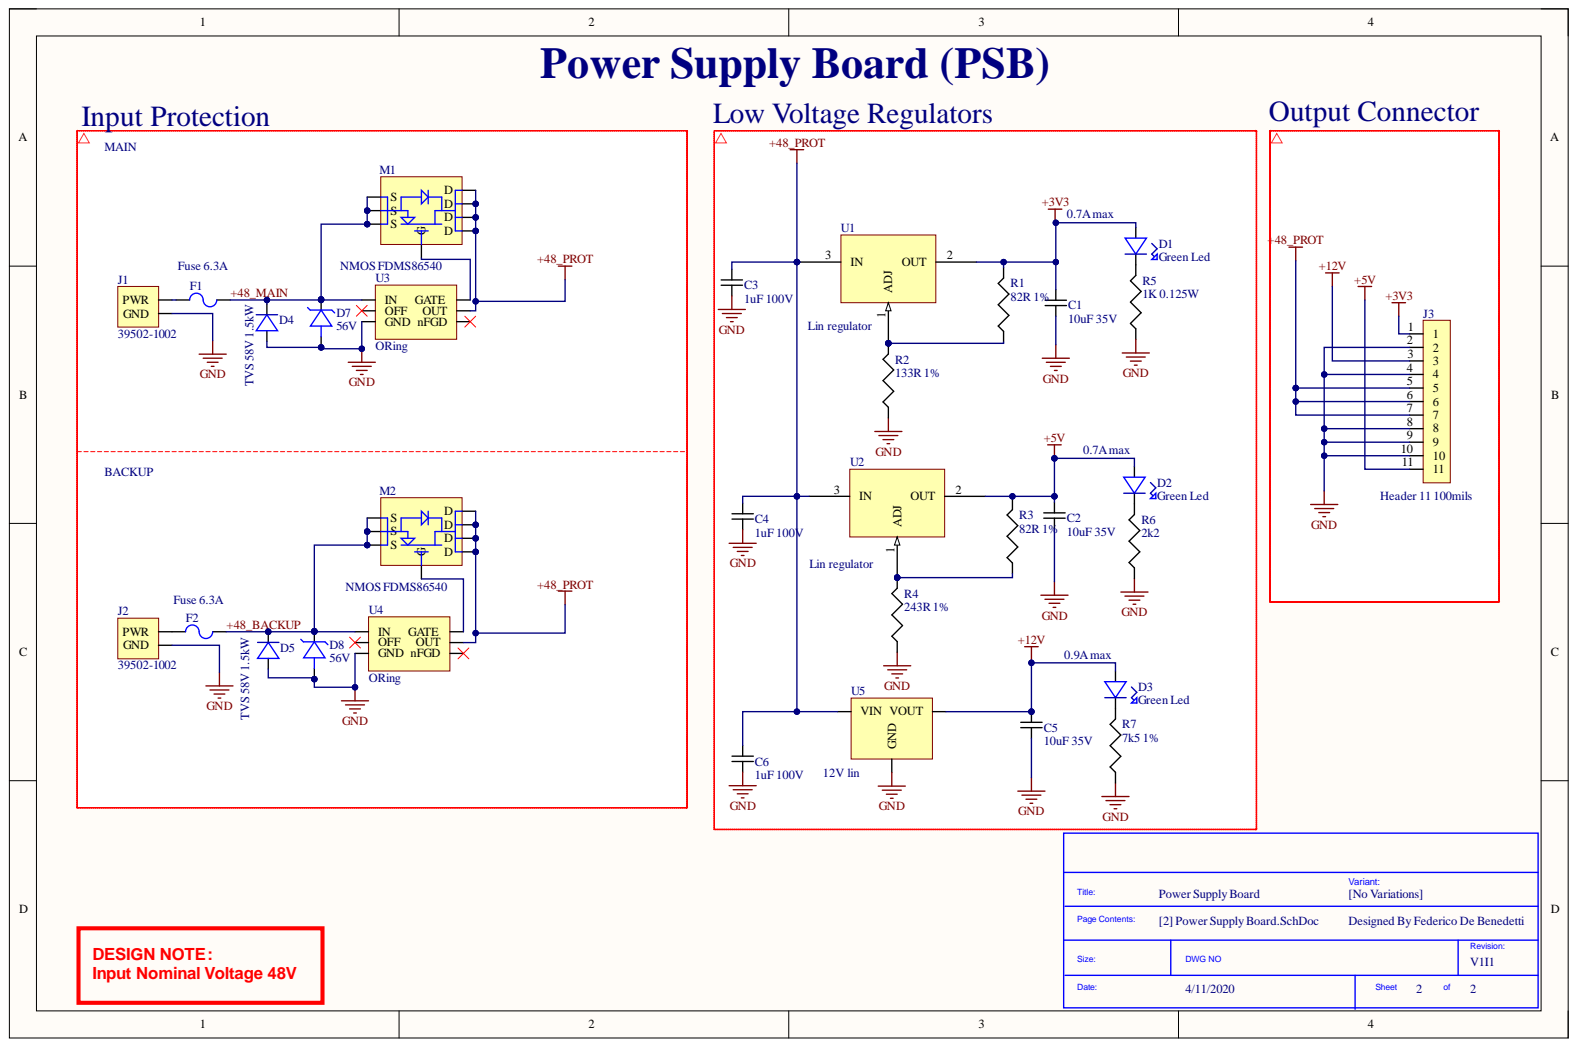
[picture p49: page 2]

Power Supply Board (PSB)

6 6
7 7
8 8
9 9

[2] Power Supply Board.SchDoc

Designed By Federico De Benedetti

Size: | DWG NO | Revision: V1I1

Date: 4/11/2020 | Sheet 2 of 2

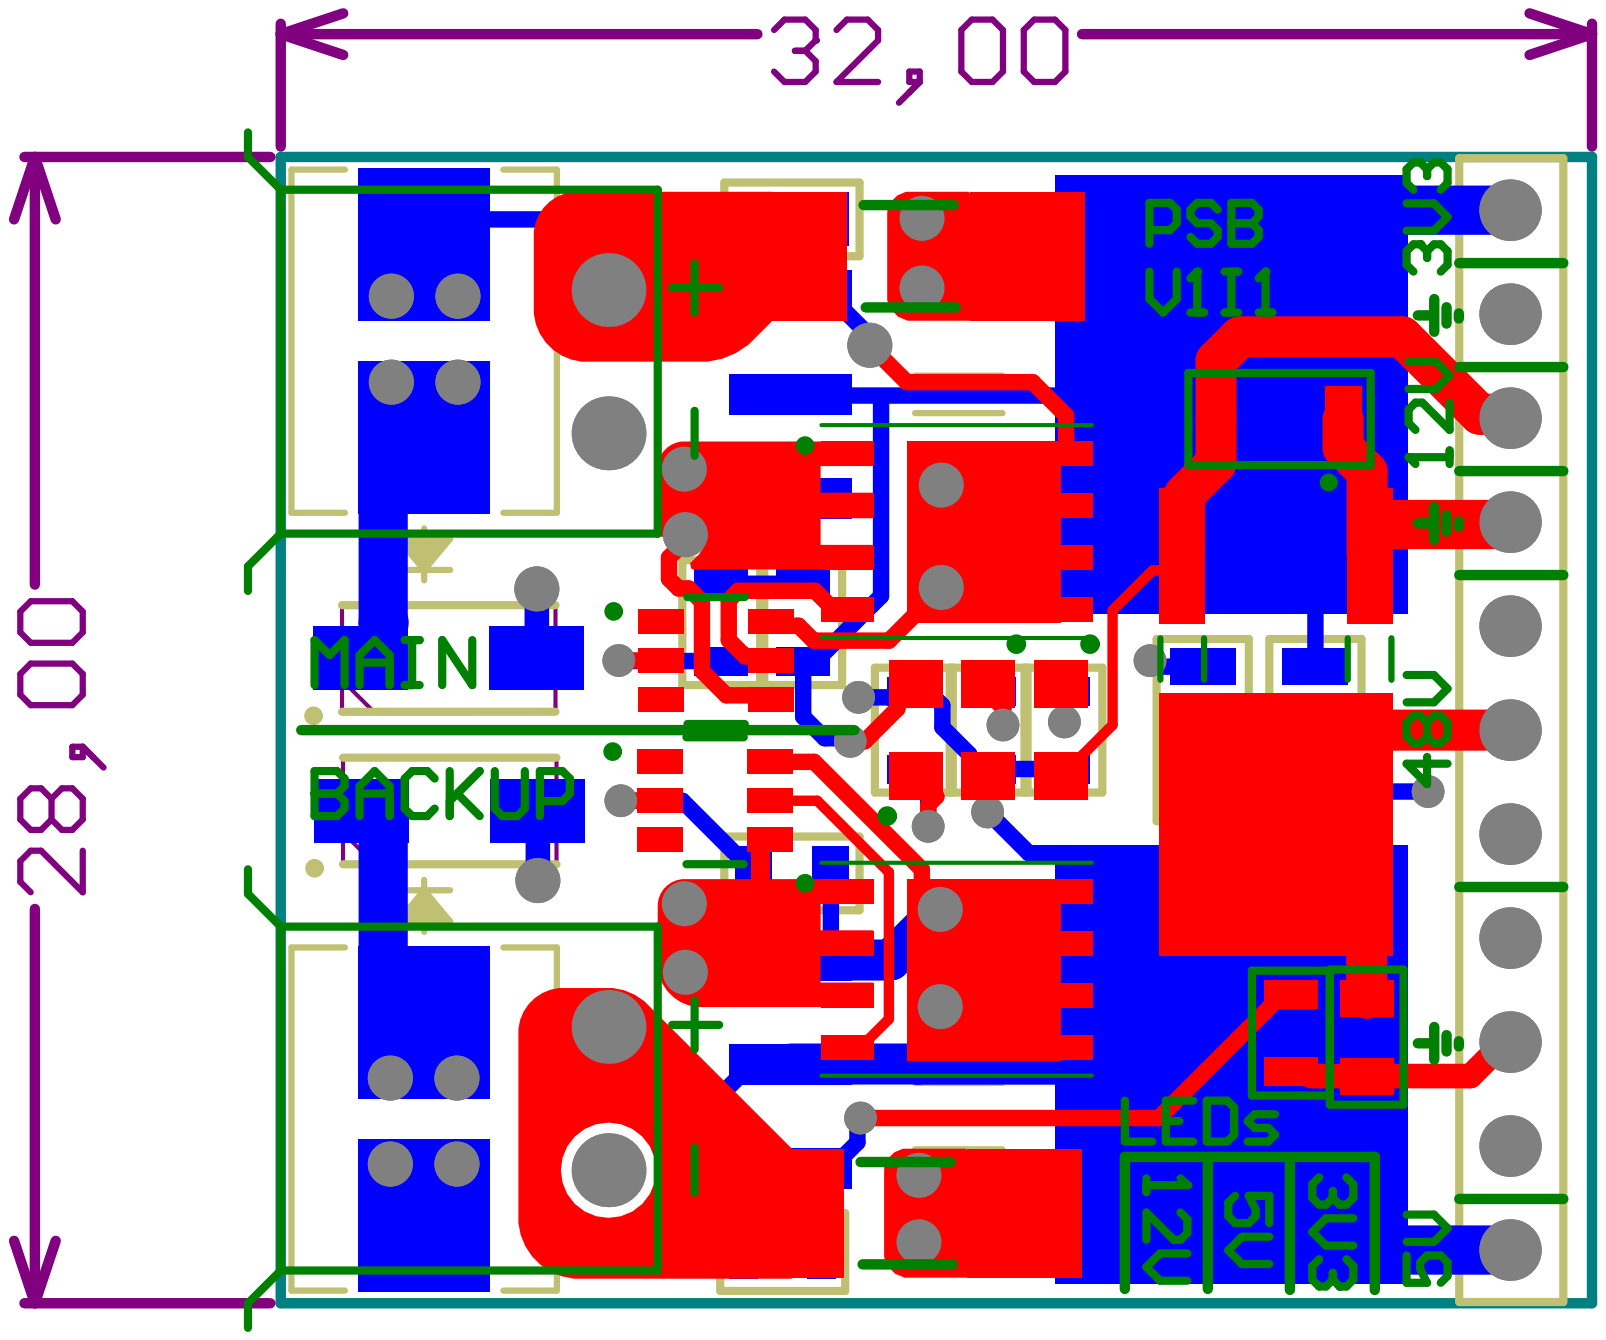
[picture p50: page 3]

Comment | Description | Designator | Footprint | LibRef | Quantity
10uF 35V | CAP CER 10UF 35V X7R 1206 | C1, C2, C5 | Capacitor 1206 | GMK316AB7106KL-TR | 3
1uF 100V | Cap Ceramic 1uF 100V X7S 10% Pad SMD 0805 125C T/R | C3, C4, C6 | C0805 | GRM21BC72A105KE01 L | 3
Green Led | LED 0805 GREEN 20MCD | D1, D2, D3 | Led Green 0805 Dialight 5988 | 598-8170-107F | 3
TVS 58V 1.5kW | TVS DIODE 58VWM 93.6VC SMC | D4, D5 | TVS SMCJSeries | SMCJ58CA | 2
56V | Diodes Zener 56V 1.5W | D7, D8 | DIODE ZENER 56V 1SMA5943BT3G | 1SMA5943BT3G | 2
Fuse 6.3A | Fuse 2410 SMD FAST-ACTING PRECISION W | F1, F2 | FUSE SMD 6.3A SF-2410FP630W | SF-2410FP630W-2 | 2
39502-1002 | Terminal Block,2 Contacts,PIN ;RoHS Compliant: Yes | J1, J2 | Terminal Block 0395021002 | 39502-1002 | 2
Header 11 100mils | HEADER 11 pins Male 2.54MM | J3 | Header 11 pos Male 2.54 | PREC011SAAN-RC | 1
NMOS FDMS86540 | MOSFET 60V N-Channel PowerTrench MOSFET | M1, M2 | NMOS FDMS86540 | FDMS86540 | 2
82R 1% | Res Thick Film 0805 82R, 150 V, Thick Film, 125mW | R1, R3 | Resistor R0805 Panasonic ERJ | ERJ6ENF82R0V | 2
133R 1% | Res Thick Film 0805 133R, 125mW, 1%, 150 V | R2 | Resistor R0805 Panasonic ERJ | ERJ-6ENF1330V | 1
243R 1% | Res Thick Film 0805 243 R, 125mW, 1%, 150 V | R4 | Resistor R0805 Panasonic ERJ | ERJ-6ENF2430V | 1
1K 0.125W | Res 0805, 1K, 0.125W | R5 | Resistor R0805 Panasonic ERJ | ERJ6ENF1001V | 1
2k2 | Res Thick Film 00805 2.2K 1% 1/8W 0805 | R6 | Resistor R0805 Panasonic ERJ | ERJ6ENF2201V | 1
7k5 1% | Res Thick Film 7.5k 125mW, ±1%; | R7 | Resistor R0805 Panasonic ERJ | ERJ-6ENF7501V | 1
Lin regulator | Linear Regulator, Adjustable, 20V primary input, 1.25V to 125V/700mA/1 Output, TO-263-3 | U1, U2 | Linear TL783CKTTR | TL783CKTTR | 2
ORing | IC OR CTRLR N+1 6SOT | U3, U4 | LM5050 | LM5050MK-2/NOPB | 2
12V lin | LINEAR 12V 60MA TO252-3 | U5 | Linear ZXTR2012K | ZXTR2012K-13 | 1

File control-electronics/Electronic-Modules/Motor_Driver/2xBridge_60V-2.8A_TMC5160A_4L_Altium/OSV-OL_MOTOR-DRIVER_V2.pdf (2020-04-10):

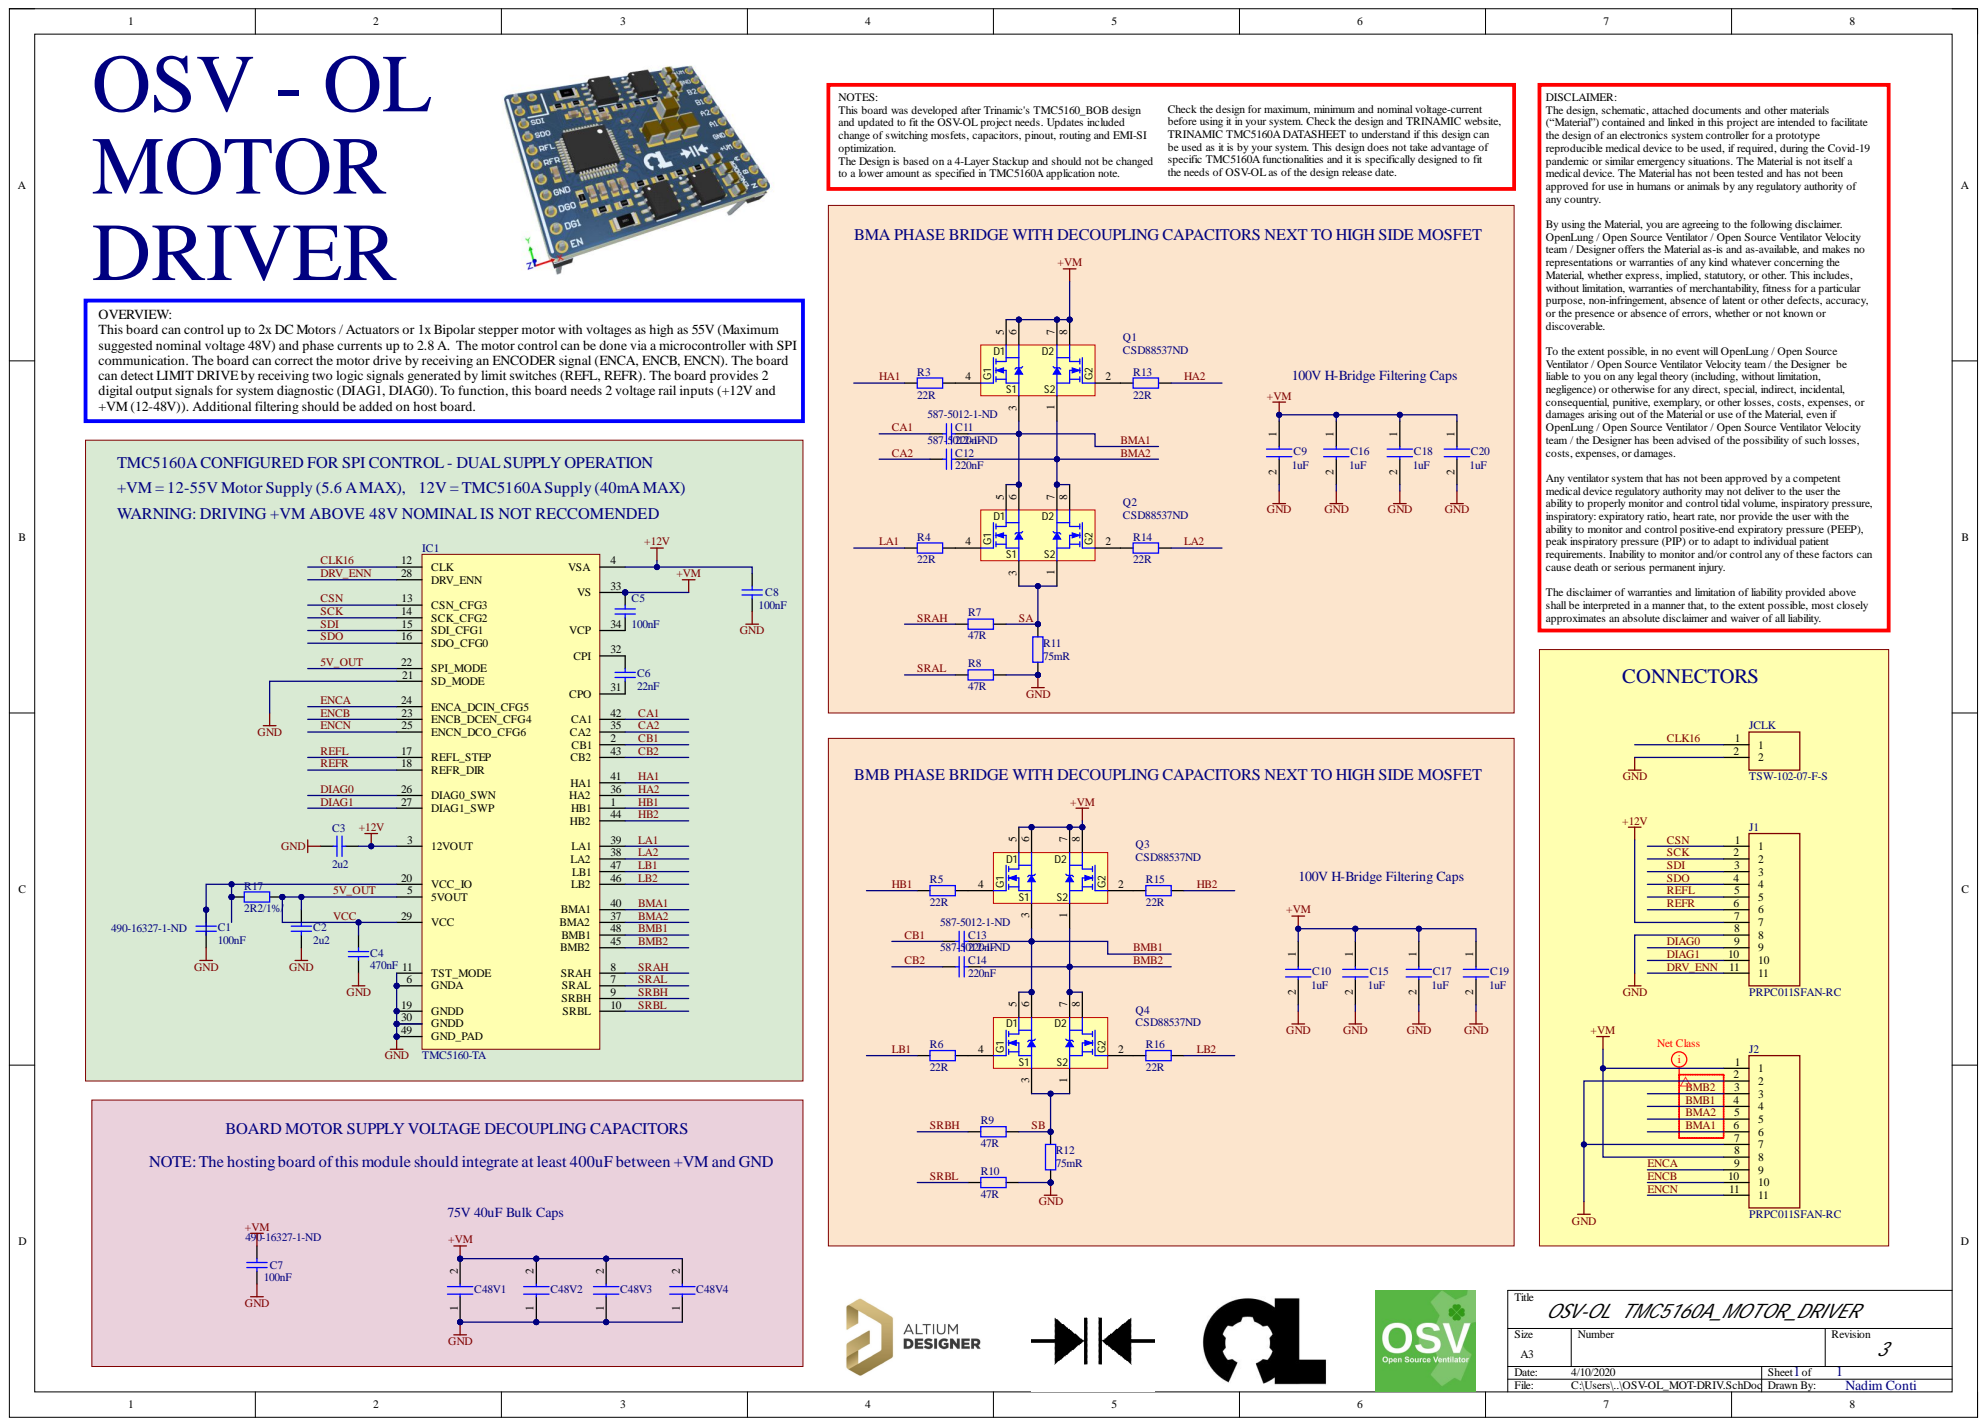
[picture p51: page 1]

DISCLAIMER:
The design, schematic, attached documents and other materials
(“Material”) contained and linked in this project are intended to facilitate
the design of an electronics system controller for a prototype
reproducible medical device to be used, if required, during the Covid-19
pandemic or similar emergency situations. The Material is not itself a
medical device. The Material has not been tested and has not been
approved for use in humans or animals by any regulatory authority of
any country.

This board was developed after Trinamic's TMC5160_BOB design
and updated to fit the OSV-OL project needs. Updates included
change of switching mosfets, capacitors, pinout, routing and EMI-SI
optimization.
The Design is based on a 4-Layer Stackup and should not be changed
to a lower amount as specified in TMC5160A application note.

before using it in your system. Check the design and TRINAMIC website,
TRINAMIC TMC5160A DATASHEET to understand if this design can
be used as it is by your system. This design does not take advantage of
specific TMC5160A functionalities and it is specifically designed to fit
the needs of OSV-OL as of the design release date.

BMA PHASE BRIDGE WITH DECOUPLING CAPACITORS NEXT TO HIGH SIDE MOSFET

By using the Material, you are agreeing to the following disclaimer.
OpenLung / Open Source Ventilator / Open Source Ventilator Velocity
team / Designer offers the Material as-is and as-available, and makes no
representations or warranties of any kind whatever concerning the
Material, whether express, implied, statutory, or other. This includes,
without limitation, warranties of merchantability, fitness for a particular
purpose, non-infringement, absence of latent or other defects, accuracy,
or the presence or absence of errors, whether or not known or
discoverable.

OVERVIEW:
This board can control up to 2x DC Motors / Actuators or 1x Bipolar stepper motor with voltages as high as 55V (Maximum
suggested nominal voltage 48V) and phase currents up to 2.8 A. The motor control can be done via a microcontroller with SPI
communication. The board can correct the motor drive by receiving an ENCODER signal (ENCA, ENCB, ENCN). The board
can detect LIMIT DRIVE by receiving two logic signals generated by limit switches (REFL, REFR). The board provides 2
digital output signals for system diagnostic (DIAG1, DIAG0). To function, this board needs 2 voltage rail inputs (+12V and
+VM (12-48V)). Additional filtering should be added on host board.

To the extent possible, in no event will OpenLung / Open Source
Ventilator / Open Source Ventilator Velocity team / the Designer be
liable to you on any legal theory (including, without limitation,
negligence) or otherwise for any direct, special, indirect, incidental,
consequential, punitive, exemplary, or other losses, costs, expenses, or
damages arising out of the Material or use of the Material, even if
team / the Designer has been advised of the possibility of such losses,
costs, expenses, or damages.

TMC5160A CONFIGURED FOR SPI CONTROL - DUAL SUPPLY OPERATION
+VM = 12-55V Motor Supply (5.6 AMAX), 12V = TMC5160ASupply (40mAMAX)
WARNING: DRIVING +VM ABOVE 48V NOMINAL IS NOT RECCOMENDED

Any ventilator system that has not been approved by a competent
medical device regulatory authority may not deliver to the user the
ability to properly monitor and control tidal volume, inspiratory pressure,
inspiratory: expiratory ratio, heart rate, nor provide the user with the
ability to monitor and control positive-end expiratory pressure (PEEP),
peak inspiratory pressure (PIP) or to adapt to individual patient
requirements. Inability to monitor and/or control any of these factors can
cause death or serious permanent injury.

The disclaimer of warranties and limitation of liability provided above
shall be interpreted in a manner that, to the extent possible, most closely
approximates an absolute disclaimer and waiver of all liability.

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

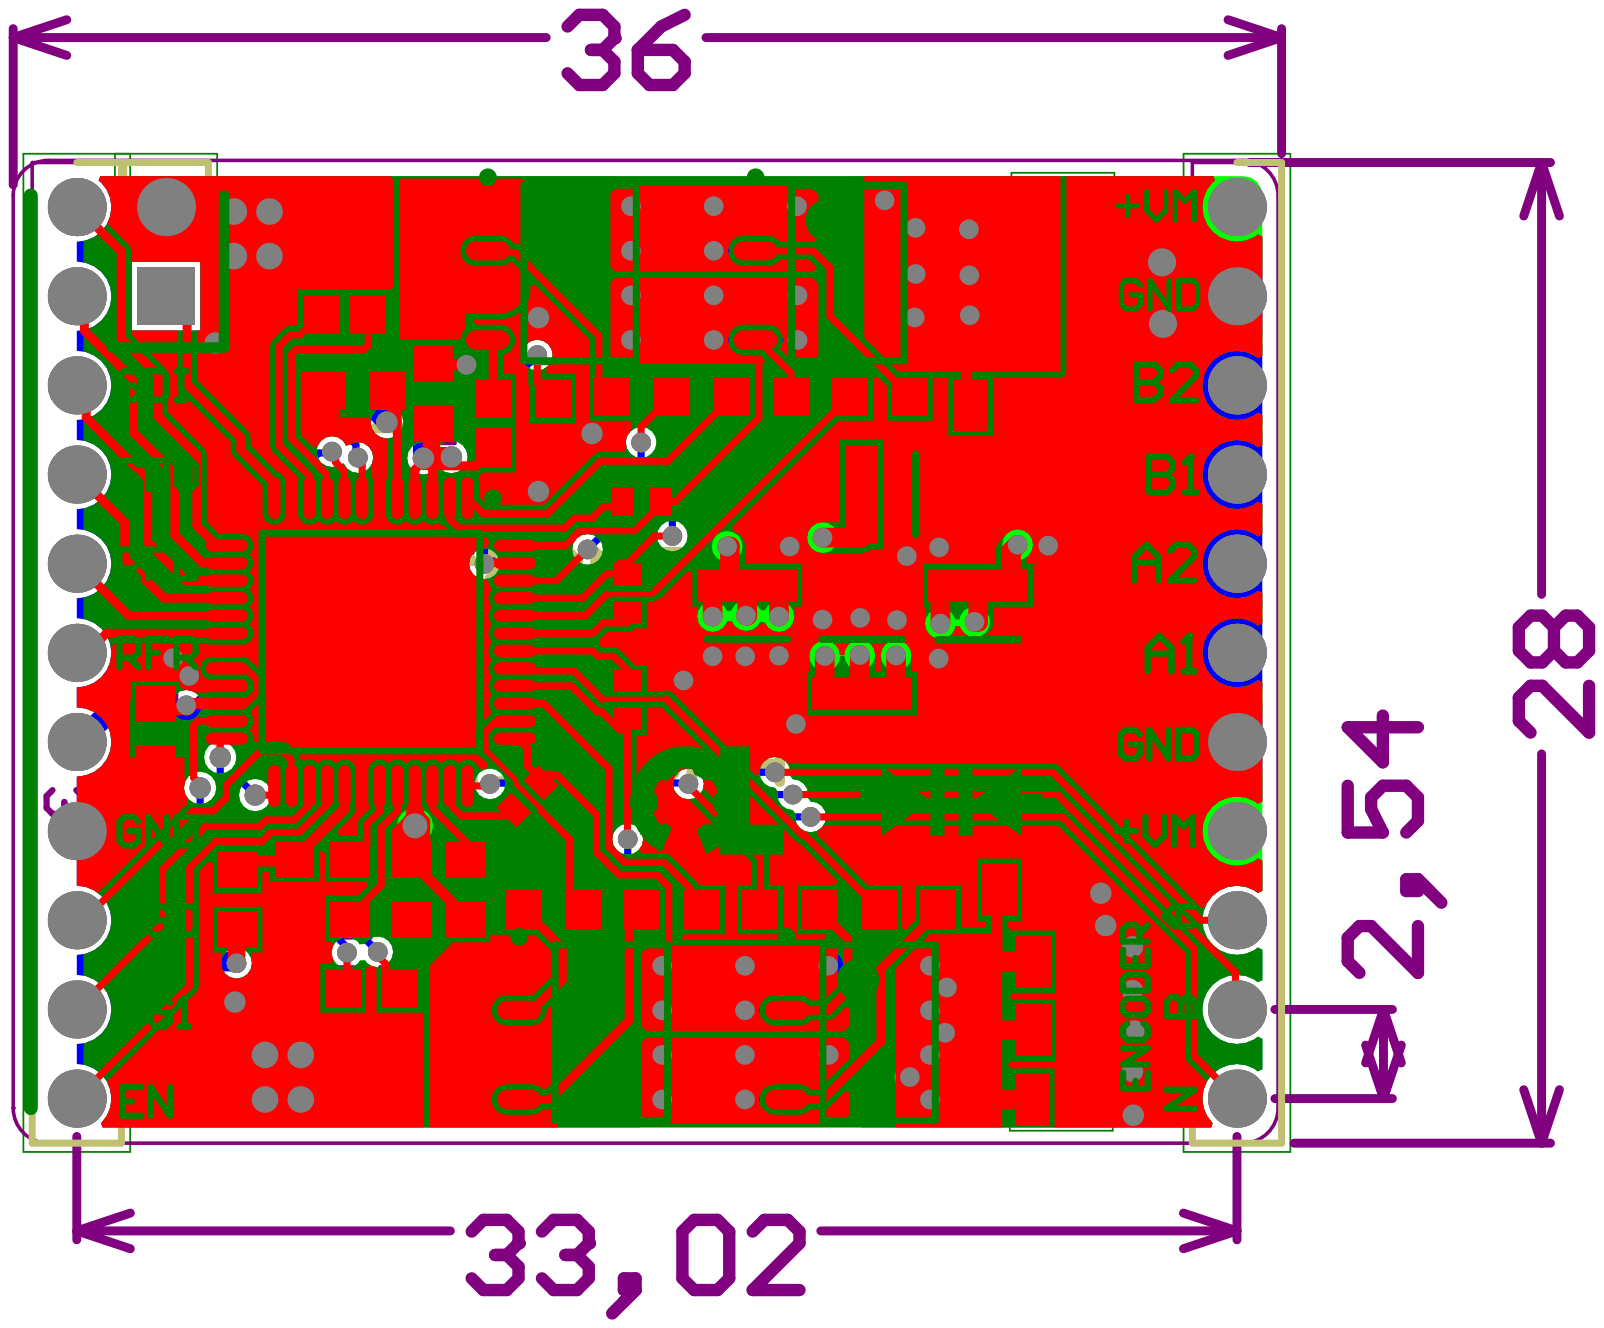
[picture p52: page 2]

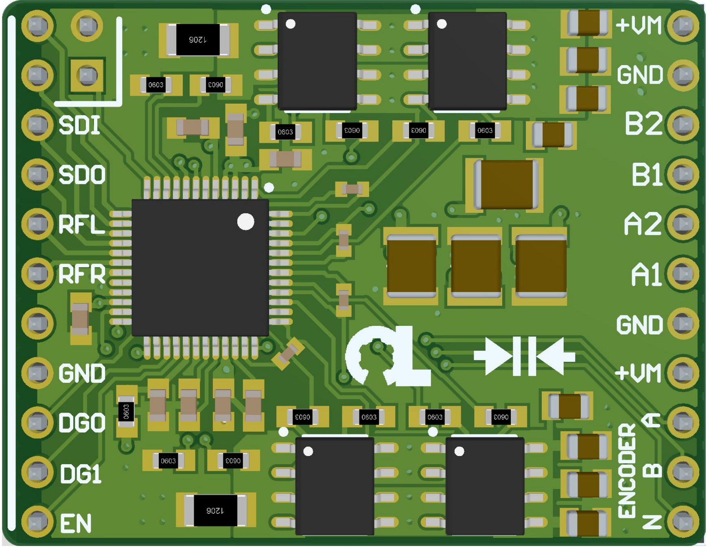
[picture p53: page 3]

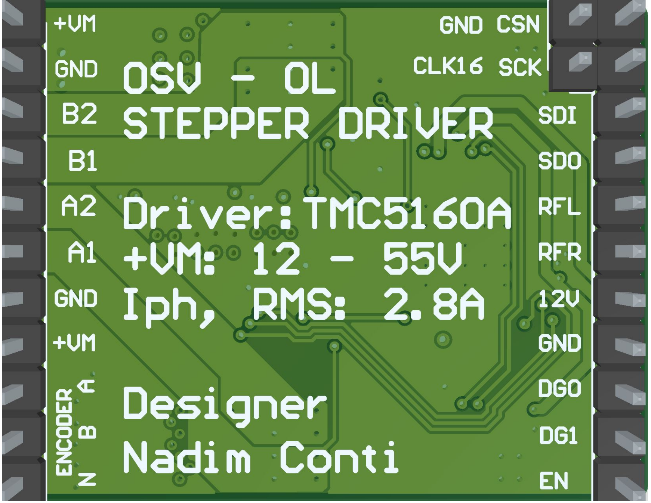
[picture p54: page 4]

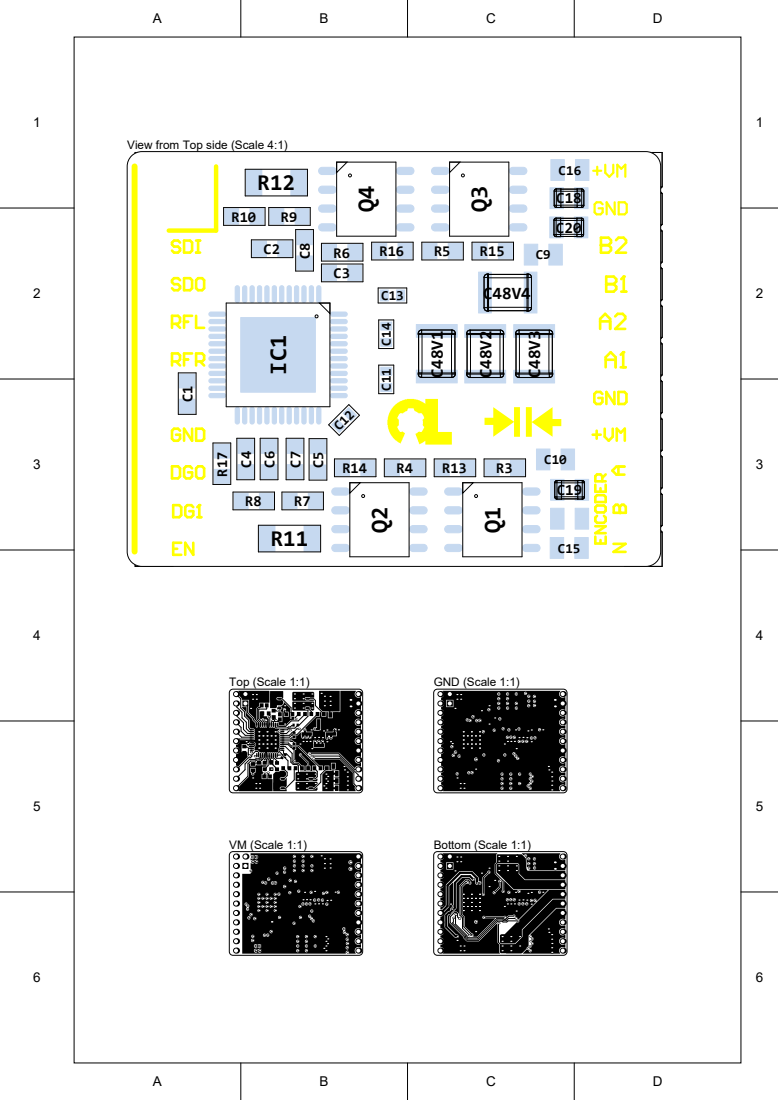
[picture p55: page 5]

View from Top side (Scale 4:1)

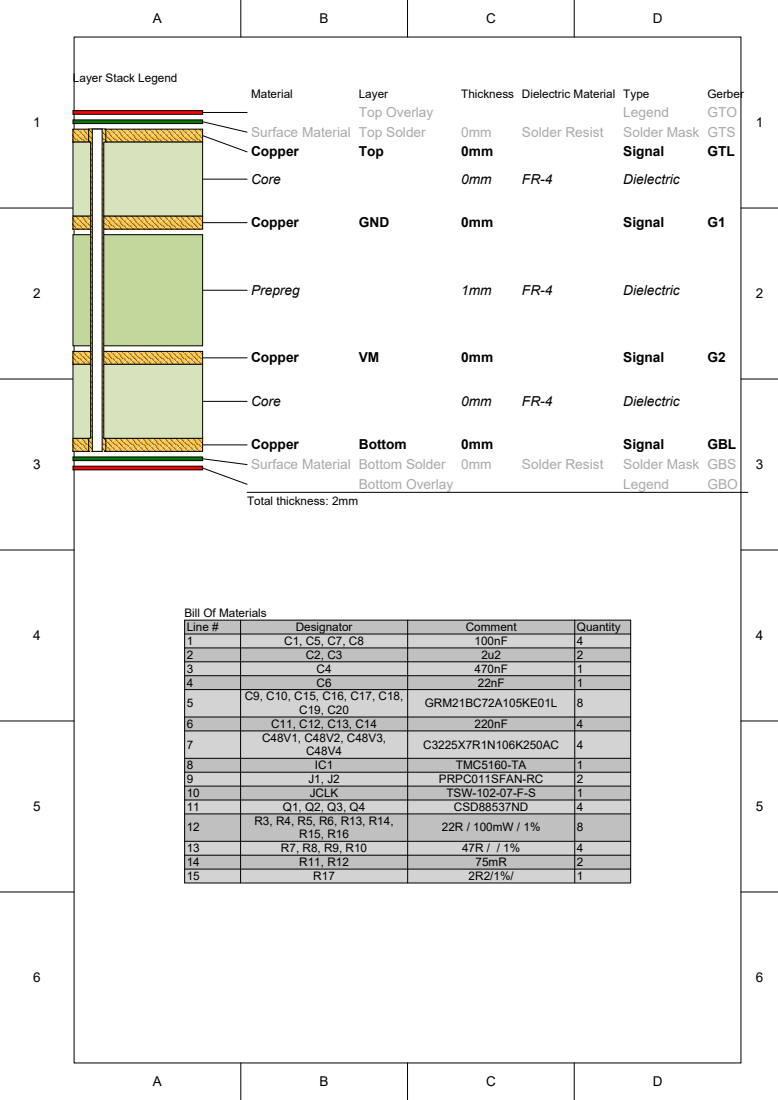
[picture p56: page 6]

Line # | Designator | Comment | Quantity
1 | C1, C5, C7, C8 | 100nF | 4
2 | C2, C3 | 2u2 | 2
3 | C4 | 470nF | 1
4 | C6 | 22nF | 1
5 | C9, C10, C15, C16, C17, C18, C19, C20 | GRM21BC72A105KE01L | 8

6 | C11, C12, C13, C14 | 220nF | 4
7 | C48V1, C48V2, C48V3, C48V4 | C3225X7R1N106K250AC | 4
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

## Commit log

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2020-03-22 adding STL and images for C7A1 #47
    [Frame_block_v1.stl, Frame_part1_v1.stl, Frame_part2_v1.stl, Frame_part3_v1.stl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]
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2020-03-22 Transfer Emergency Face Shield To New Repo
    [EmergencyFaceShield_ASM_REV0.stp, EmergencyFaceShield_ASM_REV1.stp, FL_MASK_A1.stp, FL_MASK_A1_BOTTOM.dxf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]
2020-03-23 added back panel upgrade for 6A1
    [backPanel.skp, backPanel.stl]
2020-03-23 File: "OSV-OBV-ProductComparison_A00.xlsx" This is a product comparison table between three projects: 1 - Code Life Ventilator Challenge 2 - GOV.UK: Coronavirus (COVID-19): ventilator supply specific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
    [OSV-OBV-ProductComparison_A00.xlsx]
2020-03-23 adding Autodesk Fusion assembly model for the BVM bag
    [BVM_Assembly.f3d]
2020-03-23 Add concept 6C1
    [Body.stl, Gear.stl, No_motor.stl, Trava.stl]
2020-03-23 Moved OBV XLSX spreadsheet
    [OSV-OBV-ProductComparison_A00.xlsx]
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2020-03-24 Updated names of concept directories, formatted feedback and
    [Adaptador-print1-1peca.STL, Body.stl, CONCEPT-6-PLATE_CUT.dxf, CONCEPT-6-PLATE_CUT.stl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]
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2020-03-25 C6 is still active, close #101
    [Adaptador-print1-1peca.STL, Body.stl, CONCEPT-6-PLATE_CUT.dxf, CONCEPT-6-PLATE_CUT.stl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]
2020-03-25 adding controller concept and P1A1 concept. close #102
    [bom.ods, masterComponentList.ods]
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2020-03-25 Repair models STL, add README.md concept 6C1
    [Gear.stl, No_motor.stl, Trava.stl]
2020-03-26 step file
    [belt1.STEP]
2020-03-26 STL file
    [belt1.STL]
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2020-03-26 updating components list
    [bom.ods, masterComponentList.ods]
2020-03-26 Renamed controller and sensor to include arduino
    [bom.ods, masterComponentList.ods]
2020-03-26 adding P1A1 kicad schematic for @uxvrob, close #109
    [LM2596HVS_Adjustable_Regulator.sch, P1A1_Controller_Board.sch]
2020-03-26 add P1A1 schema for @uxvrob, close #109
    [LM2596HVS_Adjustable_Regulator.sch, P1A1_Controller_Board.sch]
2020-03-26 Adjusted naming of arduino-controller and arduino-sensor, added image 8
    [bom.ods, masterComponentList.ods]
2020-03-26 added twister concept as concept 9 proposal
    [DrivePlate_2.stl, FeetDriveside_2.stl, FeetTraverse_2.stl, FootMovingsSide_2.stl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]
2020-03-26 Rename of controller to be clearer
    [bom.ods, masterComponentList.ods]
2020-03-28 Concept 6D1 : enhanced mechanics and case design (more compacte and covers ambu-bag)
    [Ventilator_6D1.blend]
2020-03-28 SolidWorks 2020 file
    [ambuBag.SLDPRT]
2020-03-29 SolidWorks 2020 ambubag moddel added
    [ambuBag.SLDPRT]
2020-03-29 SolidWorks 2020
    [CamTrack2.SLDPRT]
2020-03-29 Upload New File
    [CamTrack2.STEP]
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2020-03-31 Update concepts/ventilator-concept-12/CSA1/3D-Models/.gitkeep, concepts/ventilator-concept-12/CSA1/3D-Models/camTrack.SLDPRT, concepts/ventilator-concept-12/CSA1/3D-Models/camTrack.STEP, concepts/ven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
    [CamTrack2.SLDPRT, CamTrack2.STEP, camTrack.SLDPRT]
2020-04-01 Version C8A3
    [AMETEK-E28H47-2.1-4-12.sldasm, AMETEK-E28H47-2.1-4-12_28000_external_linear(None).sldprt, AMETEK-E28H47-2.1-4-12_28000_external_linear_nut.sldprt, Assem - Davi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]
2020-04-01 Update concepts/ventilator-concept-12/C12A1/3D-Models/.gitkeep, concepts/ventilator-concept-12/C12A1/3D-Models/camTrack.SLDPRT, concepts/ventilator-concept-12/C12A1/3D-Models/camTrack.STEP, concepts/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
    [CamTrack2.SLDPRT, CamTrack2.STEP, camTrack.SLDPRT]
2020-04-02 Move to research
    [CamTrack2.SLDPRT, CamTrack2.STEP, camTrack.SLDPRT]
2020-04-02 Organizing concept naming
    [Adaptador-print1-1peca.STL, Body.stl, CONCEPT-6-PLATE_CUT.dxf, CONCEPT-6-PLATE_CUT.stl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]
2020-04-02 rename concepts to be more intuitive
    [AMETEK-E28H47-2.1-4-12.sldasm, AMETEK-E28H47-2.1-4-12_28000_external_linear(None).sldprt, AMETEK-E28H47-2.1-4-12_28000_external_linear_nut.sldprt, Adaptador-pr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]
2020-04-02 Files Organizing
    [AMETEK-E28H47-2.1-4-12.sldasm, AMETEK-E28H47-2.1-4-12_28000_external_linear(None).sldprt, AMETEK-E28H47-2.1-4-12_28000_external_linear_nut.sldprt, Adaptador-pr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]
2020-04-02 adding design concept 14 - fully printable mechanics
    [belt_flexible.stl, guide_stopper.stl, motorplate.stl, outter_gear.stl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]
2020-04-02 Creating directories for different sub-systems.
    [AMETEK-E28H47-2.1-4-12.sldasm, AMETEK-E28H47-2.1-4-12_28000_external_linear(None).sldprt, AMETEK-E28H47-2.1-4-12_28000_external_linear_nut.sldprt, Adaptador-pr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]
2020-04-03 Update control-electronics/Electr.Sys._Concept-Specific/smb-controller-concept-1/P1A1/hmi/.gitkeep, control-electronics/Electr.Sys._Concept-Specific/smb-controller-concept-1/P1A1/makes/.gitkeep, cont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
    [bom.ods, masterComponentList.ods]
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2020-04-03 Update control-electronics/Electronic-Modules/Motor_Driver/Stepper_36V-2.8A_TMC5160/Source-files/ChangeLog.SchDoc, control-electronics/Electronic-Modules/Motor_Driver/Stepper_36V-2.8A_TMC5160/Source-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
    [ChangeLog.SchDoc, TMC5160_BOB_V1_2.PcbDoc, TMC5160_BOB_V1_2.PcbLib, TMC5160_BOB_V1_2.PrjPcb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]
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2020-04-03 Stock material proposal
    [3842535687.SLDASM, BVM_montado.sldprt, CXI v1.SLDASM, CXI v2.SLDASM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]
2020-04-04 Update control-electronics/Electronic-Modules/Motor_Driver/Stepper_36V-2.8A_TMC5160A_2Layer_Altium/.gitKeep, control-electronics/Electronic-Modules/Motor_Driver/Stepper_36V-2.8A_TMC5160A_2Layer_Altiu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
    [TMC5160A-DRIVER_Rev1.PcbDoc, TMC5160A-DRIVER_Rev1.PrjPcb, TMC5160A-DRIVER_Rev1.SchDoc]
2020-04-04 Update control-electronics/Electronic-Modules/Motor_Driver/Stepper_36V-2.8A_TMC5160_2L_Altium/Source-Files/TMC5160A-DRIVER_Rev1.PcbDoc, control-electronics/Electronic-Modules/Motor_Driver/Stepper_36V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
    [ChangeLog.SchDoc, TMC5160A-DRIVER_Rev1.PcbDoc, TMC5160A-DRIVER_Rev1.PrjPcb, TMC5160A-DRIVER_Rev1.SchDoc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]
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2020-04-04 Update control-electronics/Electr.Sys._Concept-Specific/controller-concept-1/P1A1/kicad/LM2596HVS_Adjustable_Regulator.sch, control-electronics/Electr.Sys._Concept-Specific/controller-concept-1/P1A1/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
    [LM2596HVS_Adjustable_Regulator.sch, P1A1_Controller_Board.sch]
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2020-04-04 Organizing structure
    [BVM-Body1.stl, BVM-Body2.stl, BVM-Body5.stl, BVM.stp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]
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2020-04-04 Update control-electronics/Electronic-Modules/Motor_Driver/Stepper_60V-2.8A_TMC5160A_4L_Altium/Source-files/TMC5160_BOB_V1_2.PCBDwf, control-electronics/Electronic-Modules/Motor_Driver/Stepper_60V-2.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
    [TMC5160_BOB_V1_2.PcbDoc, TMC5160_BOB_V1_2.PcbLib, TMC5160_BOB_V1_2.PrjPcb, TMC5160_BOB_V1_2.SchDoc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]
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2020-04-07 Move BVM to its own project
    [BVM-Body1.stl, BVM-Body2.stl, BVM-Body5.stl, BVM.stp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]
2020-04-07 Retire C7
    [Frame_block_v1.stl, Frame_part1_v1.stl, Frame_part2_v1.stl, Frame_part3_v1.stl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]
2020-04-07 Retire unused projects
    [3842535687.SLDASM, BVM_montado.sldprt, CXI v1.SLDASM, CXI v2.SLDASM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]
2020-04-07 retire old C8's
    [AMETEK-E28H47-2.1-4-12.sldasm, AMETEK-E28H47-2.1-4-12_28000_external_linear(None).sldprt, AMETEK-E28H47-2.1-4-12_28000_external_linear_nut.sldprt, Assem - Davi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]
2020-04-07 Organizing Template Folder
    [bom.ods]
2020-04-07 Files/Dir Organization
    [3842535687.SLDASM, AMETEK-E28H47-2.1-4-12.sldasm, AMETEK-E28H47-2.1-4-12_28000_external_linear(None).sldprt, AMETEK-E28H47-2.1-4-12_28000_external_linear_nut.s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]
2020-04-07 Update control-electronics/Electr.Sys._Concept-Specific/smb-controller-concept-1bis/P1A1/hmi/.gitkeep, control-electronics/Electr.Sys._Concept-Specific/smb-controller-concept-1bis/P1A1/makes/.gitkeep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
    [bom.ods, masterComponentList.ods]
2020-04-07 UnPack Files
    [AMETEK-E28H47-2.1-4-12.sldasm, AMETEK-E28H47-2.1-4-12_28000_external_linear(None).sldprt, AMETEK-E28H47-2.1-4-12_28000_external_linear_nut.sldprt, Assem - Davi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]
2020-04-07 Unpack Part Files from Zip
    [AMETEK-E28H47-2.1-4-12.sldasm, AMETEK-E28H47-2.1-4-12_28000_external_linear(None).sldprt, AMETEK-E28H47-2.1-4-12_28000_external_linear_nut.sldprt, Assem - Davi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]
2020-04-08 Update control-electronics/Electronic-Modules/MotherBoard-MCU/OSV-Motherboard-Mockup-Velocity/PCB_Source-files_Mockup/.gitkeep, control-electronics/Electronic-Modules/MotherBoard-MCU/OSV-Motherboard-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
    [Motherboard.PcbDoc]
2020-04-08 Adding C16A1 by @thinkandhave
    [bom.ods, thlung.scad, tubes.scad]
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2020-04-09 Sorting Desing Requirements
    [OSV-OBV-ProductComparison_A00.xlsx]
2020-04-10 Deleted control-electronics/Electronic-Modules/Motor_Driver/Stepper_60V-2.8A_TMC5160A_4L_Altium/Source-files/TMC5160_BOB_V1_2.SchLib, control-electronics/Electronic-Modules/Motor_Driver/Stepper_60V-2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
    [TMC5160_BOB_V1_2.PcbDoc, TMC5160_BOB_V1_2.PcbLib, TMC5160_BOB_V1_2.PrjPcb, TMC5160_BOB_V1_2.SchDoc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]
2020-04-10 Update control-electronics/Electronic-Modules/Motor_Driver/_Old/Stepper_36V-2.8A_TMC5160_4L_Altium/STEP-&amp;-Images/3D_TMC5160_BOB_V1.2.step, control-electronics/Electronic-Modules/Motor_Driver/_Old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
    [ChangeLog.SchDoc, TMC5160A-DRIVER_Rev1.PcbDoc, TMC5160A-DRIVER_Rev1.PrjPcb, TMC5160A-DRIVER_Rev1.SchDoc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]
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
